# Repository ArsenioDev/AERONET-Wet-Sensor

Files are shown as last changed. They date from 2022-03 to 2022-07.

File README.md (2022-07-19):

<br/>
# AERONET-Wet-Sensor
*A custom designed replacement for the consumable rain sensors you can build in your own lab for a fraction of the cost* 
## Files and guide to assemble the conductive rain sensor custom design for the NASA AERONET instruments.  
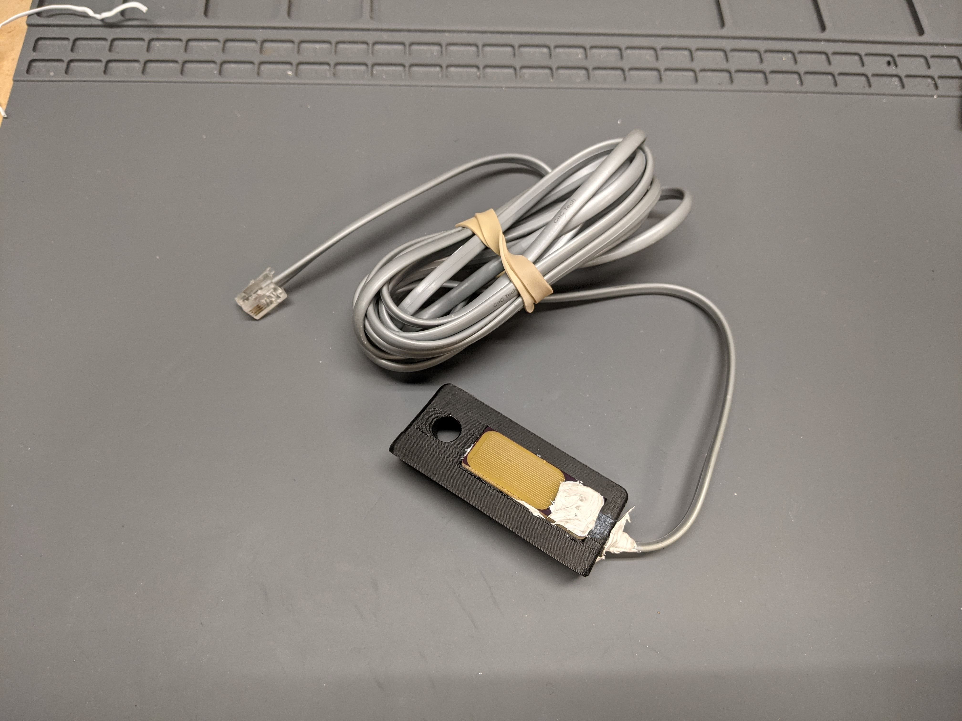
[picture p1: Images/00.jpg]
Overview image

### BOM 
1. [PCB (*MUST USE ENIG, HASL degrades far too fast*) (Check /Hardware directory for Eagle .brd files and gerbers) ](https://oshpark.com/shared_projects/1m1oY7qL)
2. [100K 0603 resistor](https://www.digikey.com/en/products/detail/yageo/RC0805FR-07100KL/730491) 
3. [3D printed support (Use PLA for cheap and easy but ASA or PETG for better UV resistance)](/Mechanical/SupportV3.stl)
4. [4Core telephone wire RJ11](https://www.digikey.com/en/products/detail/cnc-tech/530-26-04-SV-0100F/3442474) 
5. [RJ22 4P4C connector](https://www.digikey.com/en/products/detail/stewart-connector/940-SP-3044/388264) 
6. [3M 5200FC marine sealant/adhesive](https://www.3m.com/3M/en_US/p/dc/v000311743/)
----
### Build Instructions 
**Step 1** 
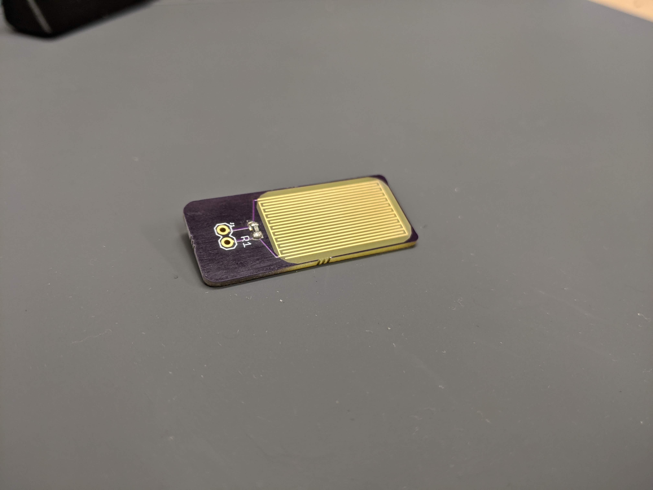
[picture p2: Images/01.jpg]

Solder 100K resistor across pads.

**Step 2** 
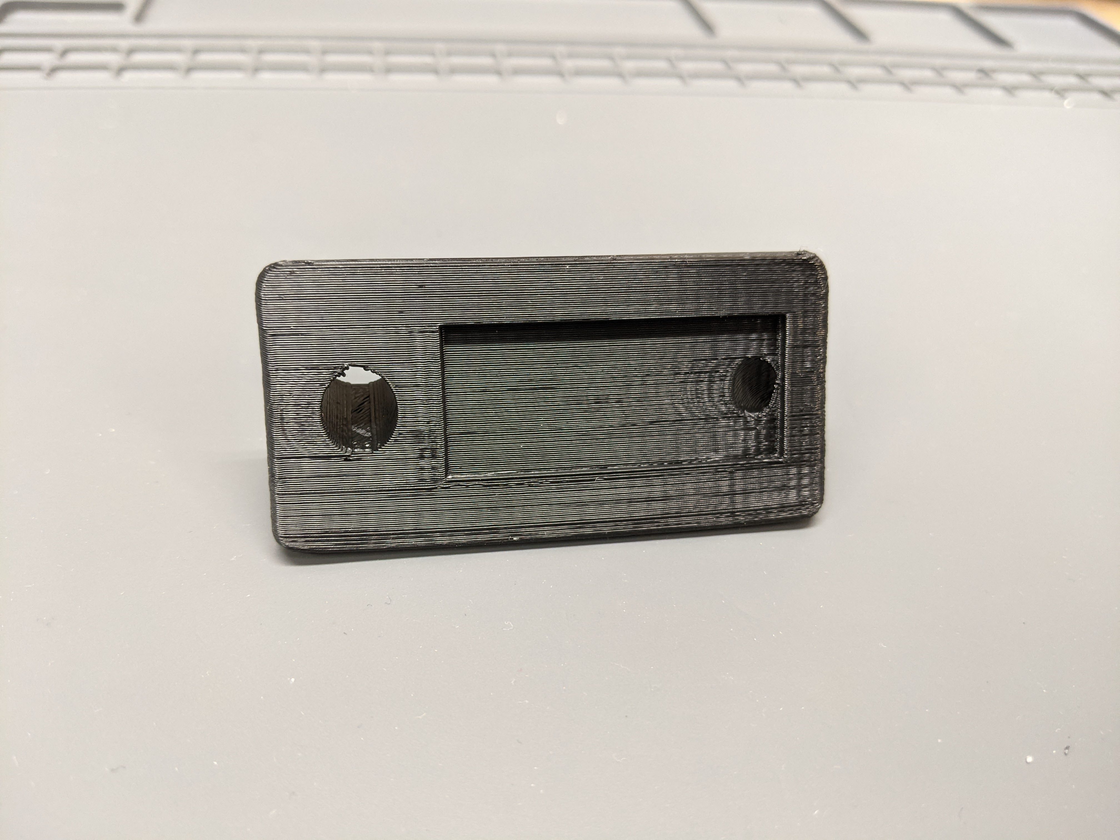
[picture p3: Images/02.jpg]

Print support (.2 layer height, 30% infill, standard temps and feed rates).

**Step 3** 
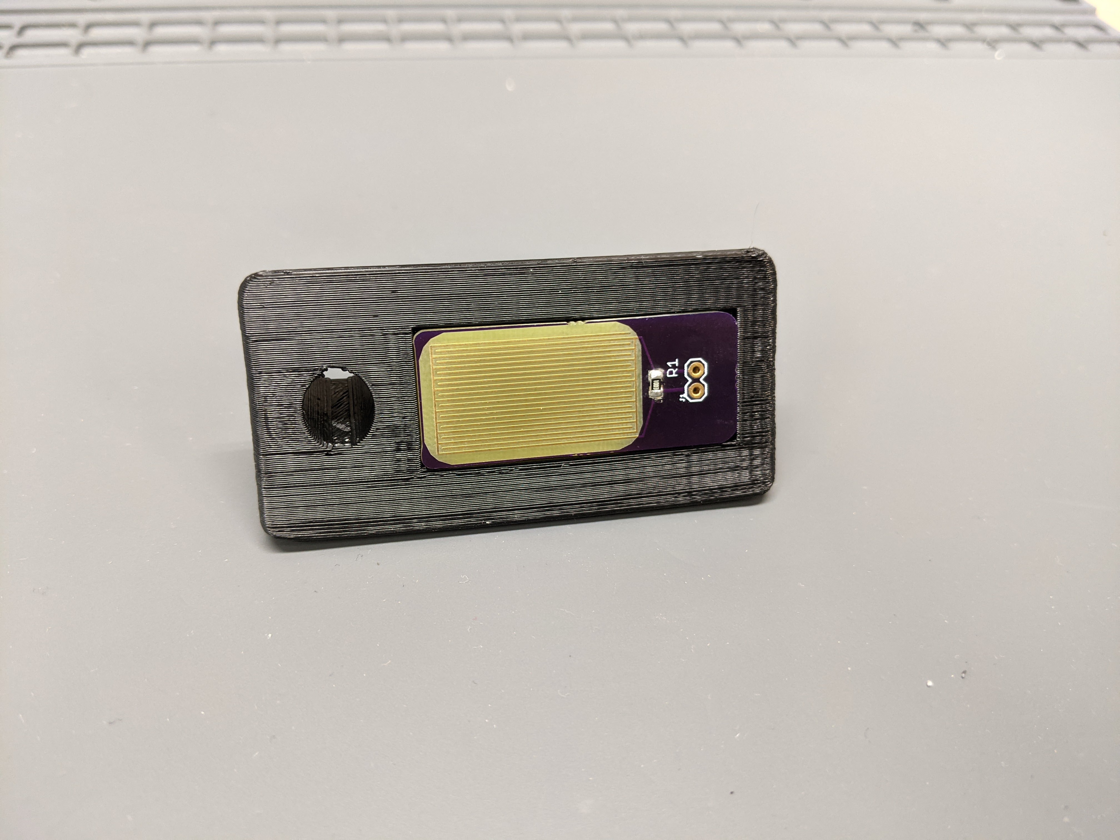
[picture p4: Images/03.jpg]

Fit check PCB, should be slightly snug.

**Step 4** 
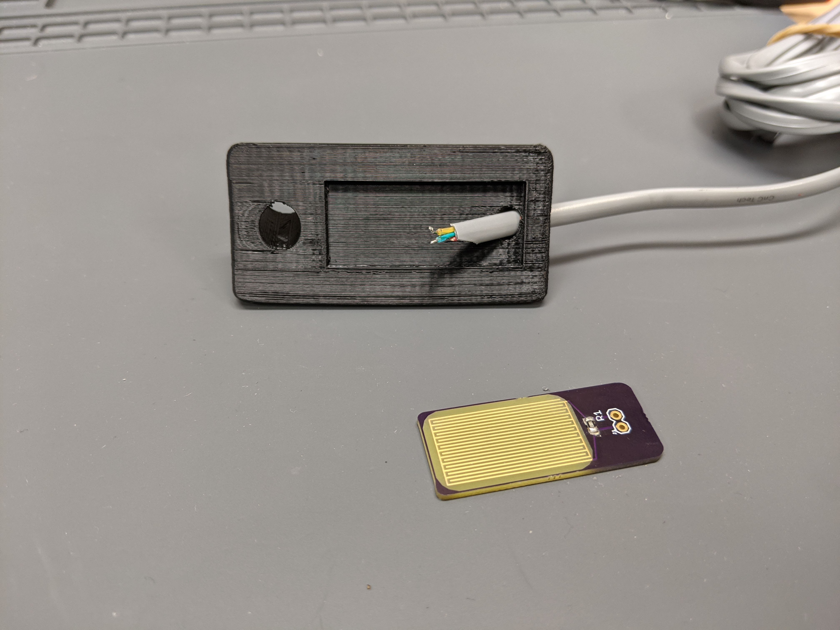
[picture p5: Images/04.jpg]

Strip end of 4C cable, seperate out Yellow and Green, tin ends, thread through cable pass.

**Step 5** 
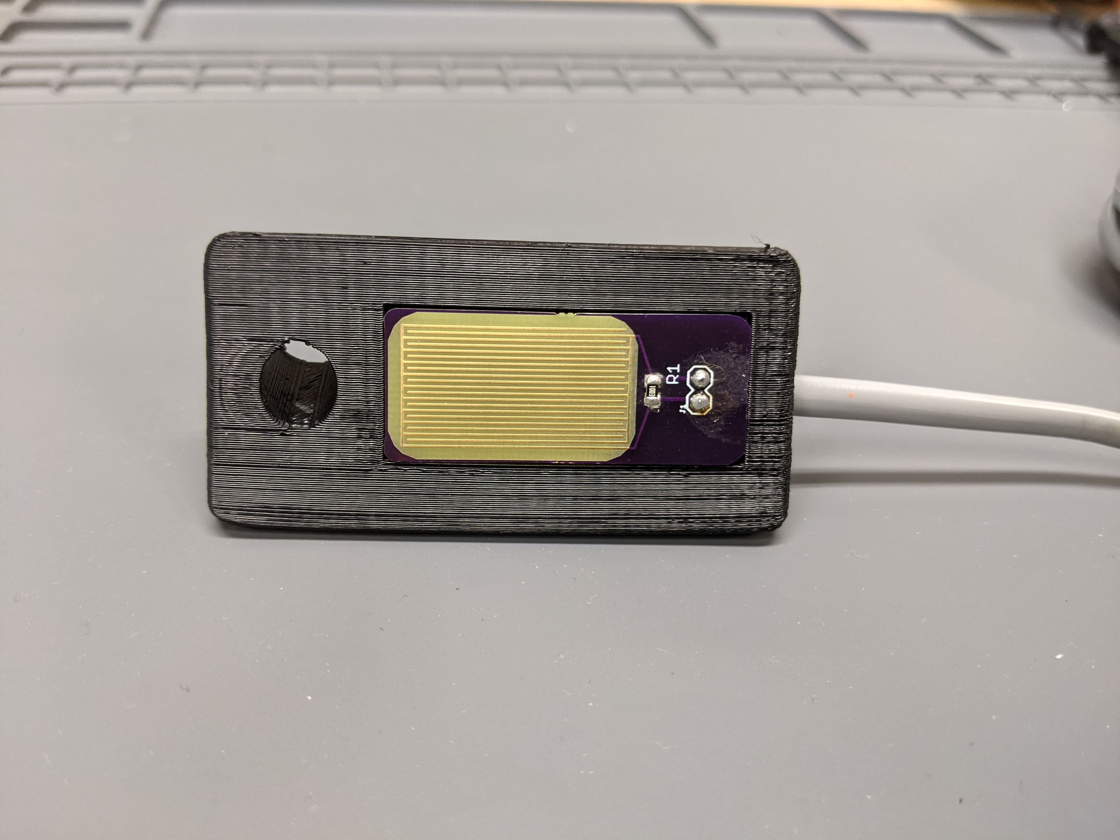
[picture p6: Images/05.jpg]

Solder conductors to through holes on PCB, polarity doesn't matter then add adhesive under PCB, snug into pocket. 

**Step 6** 
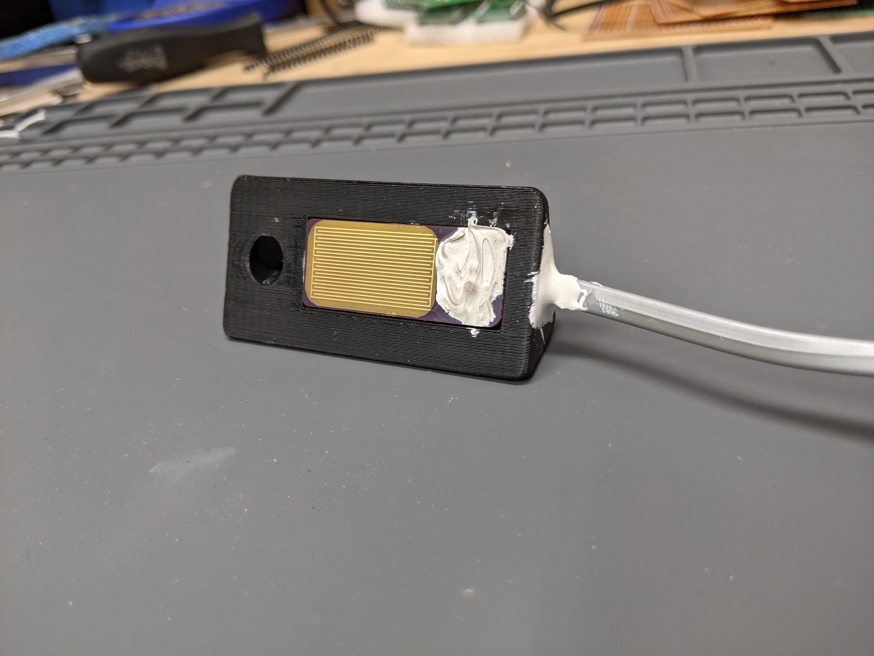
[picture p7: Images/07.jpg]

Fill the cable pass with sealing adhesive, add strain relief fillet and cover resistor and solder points. 

**Step 7** 
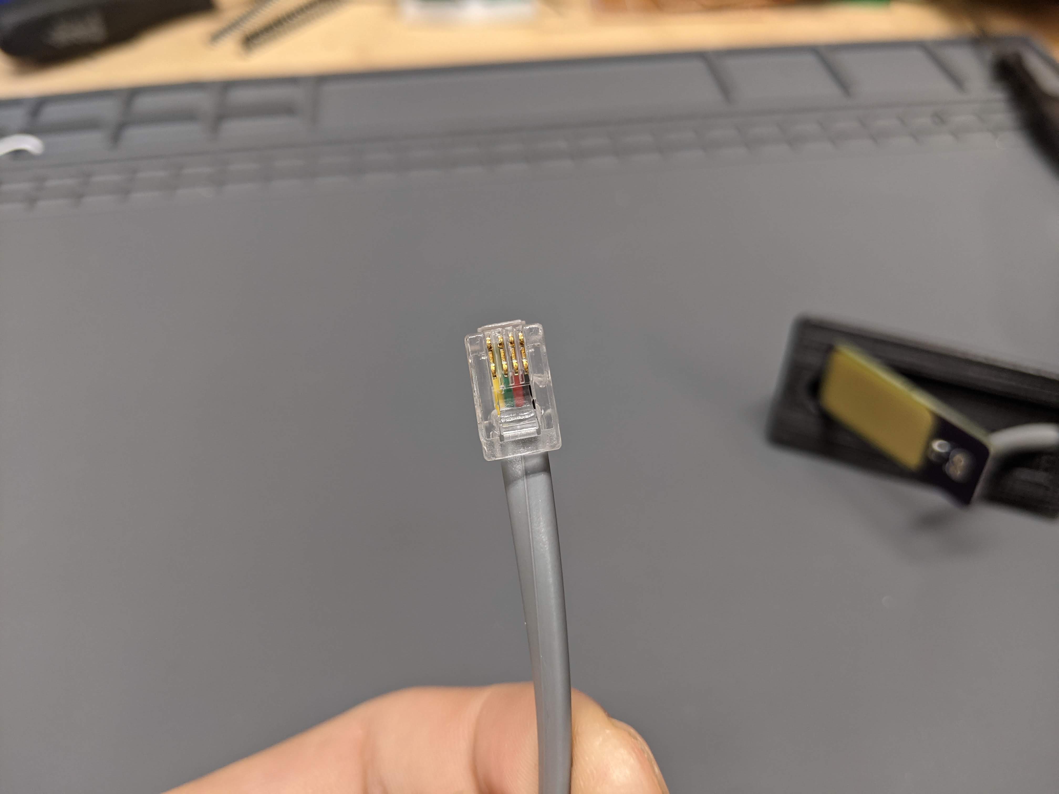
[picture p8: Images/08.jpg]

Crimp 4P4C connector according to the image, looking down at tab yellow to the right, at terminals, yellow to the left. 

***Let cure and you're done!***

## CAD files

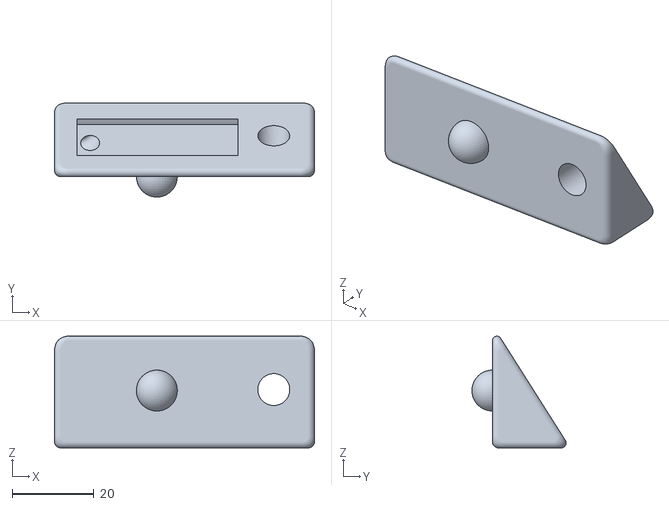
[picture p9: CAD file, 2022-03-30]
Mechanical/SupportV3.stl
63.5 x 23.0 x 27.3

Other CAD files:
Mechanical/SupportV3.f3d

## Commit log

2022-03-30 Add images of assembly process.
2022-03-30 Added folders
    [SupportV3.f3d, SupportV3.stl, WetSensorV3.brd]
2022-04-04 Update resistor
